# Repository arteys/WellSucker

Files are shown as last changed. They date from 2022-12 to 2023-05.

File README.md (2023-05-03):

# WellSucker
This project is dedicated to the development of silicone inserts in culture plastic. These will block cells from growing in a particular area, after which they are removed and it becomes possible to study the migration of cells to an empty site. I tried just flat silicone pieces, but they didn't hold well, especially in liquid. So now these things are arranged like suction cups. For 24 well plates, I made inserts with a diameter of 6 and 7 mm. There are some other options, but I'll post them later.

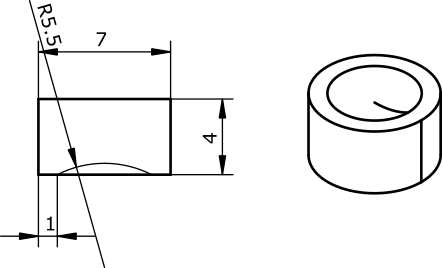
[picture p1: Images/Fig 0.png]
Sketch


To make such inserts, you need to print a mold on an MSLA 3D printer, and then pour two-component silicone into it. After hardening, the inserts are ready for use.

# 3d printing
I printed molds on a MSLA 3D printer (Anycubic Photon S) from a standard (Translucent Green) resin. For all printers and resins, different print settings are used, so there is not much point in applying mine here. Molds are printed strictly horizontally, flat, without any support. Printing at an angle greatly complicates the geometry of the parts due to the approximation of a complex shape by voxels, and the resulting inserts will not stick to the plastic reliably. Molds are designed in such a way that they are separated from the table without any problems.
There are different approaches to cleaning up objects after MSLA printing. I first wash them in dirty alcohol (IPA, although ET-OH also works fine), poured into a small container from IKEA, then for 15 minutes I wash it in an Anycubic Wash'n'Cure station in a slightly cleaner one. Finally, I flush them with a jet of alcohol from a squirt bottle and blow compressed air from a can (the one for cleaning computers) to remove all the alcohol.

Finally, I cure the objects in the same station (15 min), positioning them at such an angle that the ultraviolet accurately penetrates the cells. It is cells who must be reliably illuminated so that silicone does not stick to them later.

# The choice of silicone
This is the tricky part. Staying in the ideology of accessibility and DIY, I used the usual model two-component silicone available in the hobby store.
Two-component platinum-based silicones definitely do not work - there is some kind of reaction between the silicone and the printed part and the silicone does not polymerize.
Tin-based silicones remain, they generally work well. However, not all, I have met at least one that sticks to MSLA printed parts absolutely tightly and then it is impossible to separate the finished inserts. Accordingly, if someone decides to make such inserts, silicone will have to be selected empirically.
I didn't use any chemical separators because I didn't want to add their remnants to the biological medium.

## Step 1 and 2
Two-component silicone is mixed according to the manufacturer's instructions and poured into the wells. If the silicone is viscous, then the molds may have to be evacuated. I used a fairly fluid one, so there were no problems with bubbles.
However, if bubbles form in the finished inserts, they will spoil everything, in which case the molds with silicone must be evacuated. A certain amount of silicone may leave the wells - the most important thing is that their bottom is evenly covered, silicone can always be added after vacuuming.

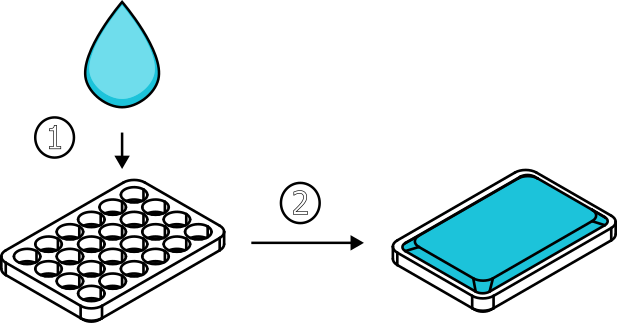
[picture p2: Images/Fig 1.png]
Step 1 and 2


## Step 3
But the next part requires some skill. With a wooden spatula (or any flat tool that you don’t mind throwing away later), you need to remove excess silicone, which will definitely be. The easiest way is to place the tool at an angle to the mold and, as it were, cut off all excess silicone. Ideally, the wells should be filled exactly to the edge, but no more. You can try to remove the excess with a cloth, but this is not very convenient.

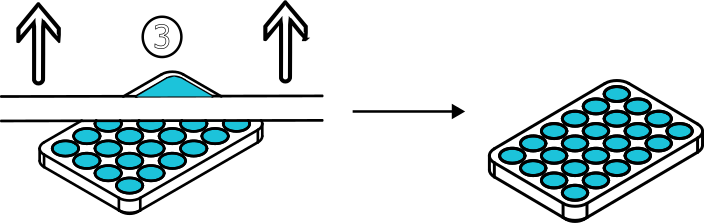
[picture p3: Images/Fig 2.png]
Step 3


After the silicone has hardened, the inserts can be removed with tweezers. Normally, they are removed quite easily, but if they stick so that they are torn to pieces, this silicone is probably not suitable.

## Inserts in cells of cultural plate
After being removed from the molds, the inserts can be sterilized with ethyl alcohol. I have not tried other methods of sterilization, although they certainly exist. Ethanol sterilization requires inserts to be placed in 70% ethanol for several minutes, after which they are removed, dried and placed in phosphate buffer or any other sterile liquid to remove residual ethanol.
Finally the inserts are ready to use. In order to install the insert into the cell of the plate, it is worth using tweezers. The most important thing is to determine where the insert has the top, it is more shiny, and the bottom is matte. Accordingly, the lower part of the insert is placed on the bottom of the well and gently pressed with tweezers from above. This is also a skill, however by the middle of the first 24 well plate it starts to come easy.
It is worth adding cells to the plate with relative accuracy. If you fill them too hard, you can wash off the insert, although this is unlikely.

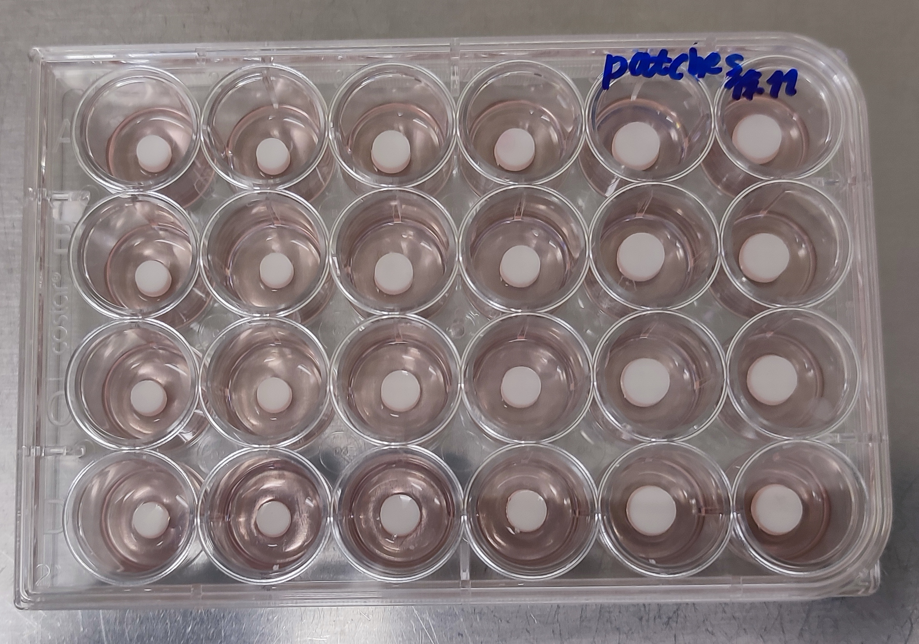
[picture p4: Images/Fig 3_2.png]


**WARNING:** These silicone inserts are amazingly bouncy. If they are pressed too hard and then released abruptly, they can jump to the other end of the laminar flow hood and fall into the vents.

## Inserts, view from the back of the plate
To make sure the inserts stick, you can turn the plate upside down. If the inserts are held securely they will of course not fall off if everything is done correctly.

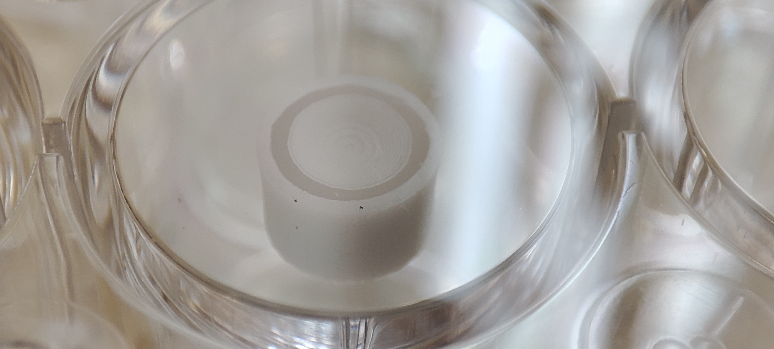
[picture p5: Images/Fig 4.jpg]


## Cells after removal of the insert
The next day, you can remove the inserts from the cells with tweezers and see something like this. I have not observed any significant cellular toxicity from silicone, but I may have been lucky with the choice of silicone. These are Vero culture cells, but experiments were also carried out with others cell lines.
Cells in plate

## Featured in
https://doi.org/10.3390/ijms24098150

## License
This project is open-source and is released under the CERN open hardware license. 
All files have been designed using  [FreeCAD](https://www.freecadweb.org/), illustrations made in FreeCAD and [Inkscape](https://inkscape.org/).

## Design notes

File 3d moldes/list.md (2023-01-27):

Model file for molds with a diameter of 6 and 7 mm

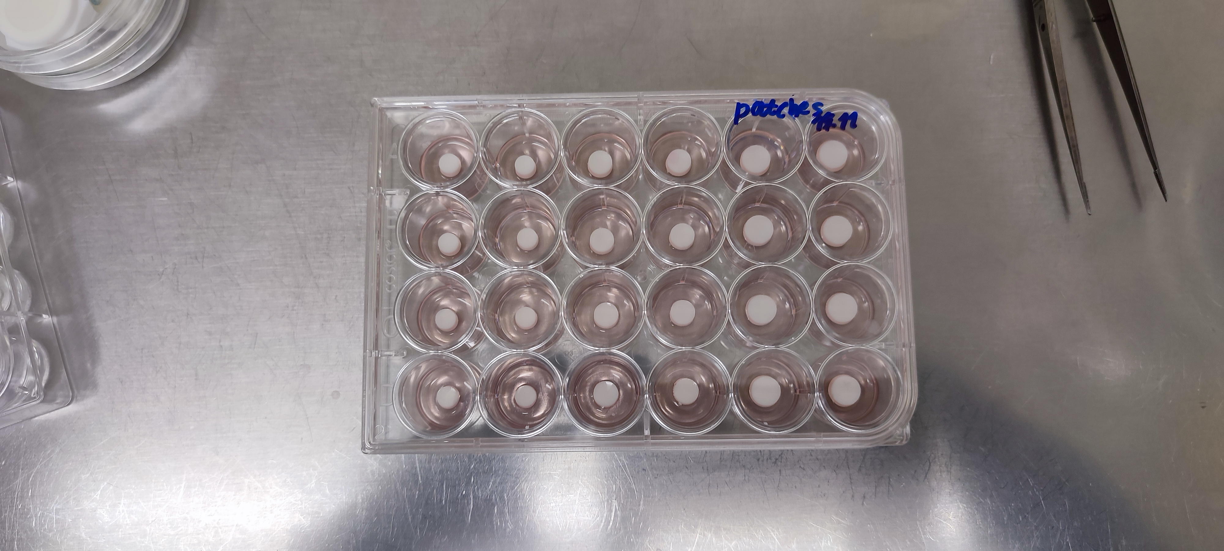
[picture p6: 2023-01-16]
Images/Fig 3.jpg

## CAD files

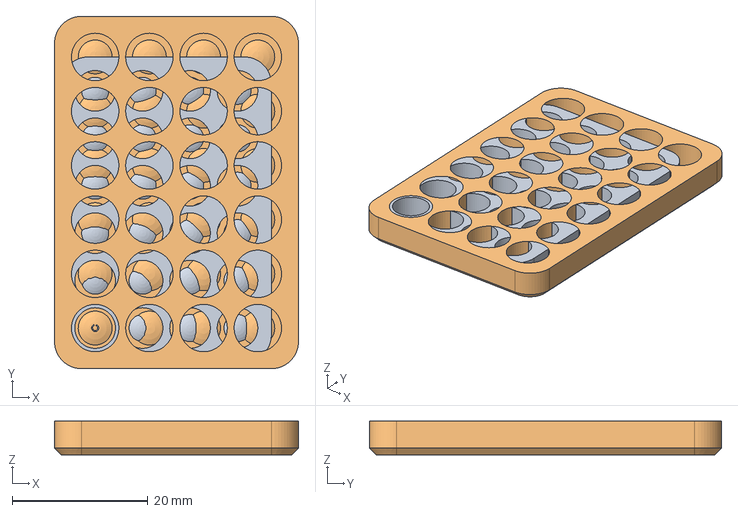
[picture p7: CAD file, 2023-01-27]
3d moldes/D6 and D7.FCStd
36.0 x 52.0 x 5.00 mm
D6
D7

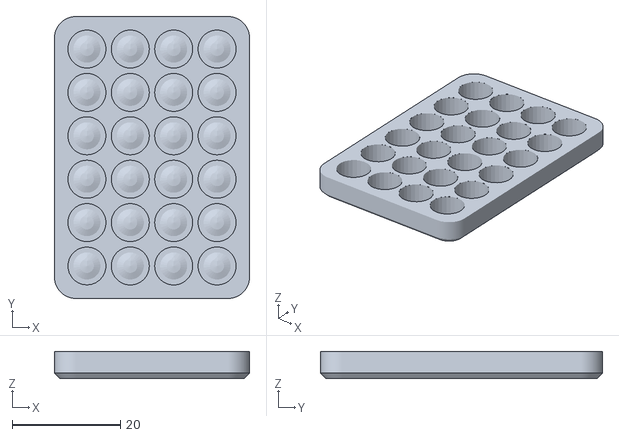
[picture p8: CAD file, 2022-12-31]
STL/D7 mold.stl
36.0 x 52.0 x 5.00

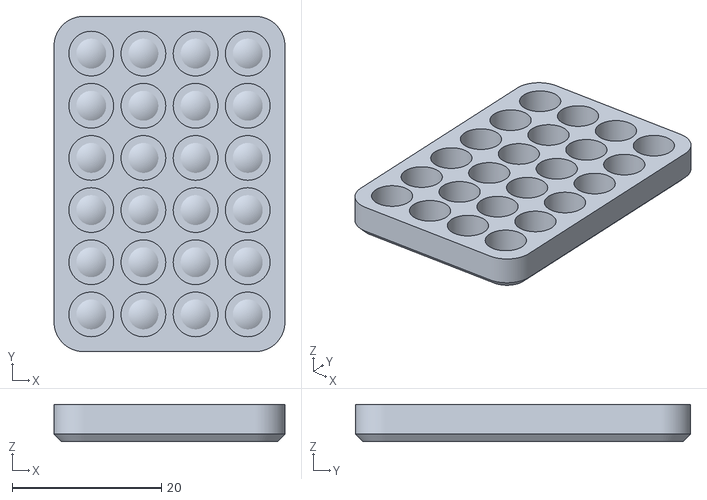
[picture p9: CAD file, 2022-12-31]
STL/D6 mold.stl
31.0 x 45.0 x 5.00

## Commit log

2023-01-16 Photos of inserts in the wildes
2023-01-25 New version of the plate with inserts photo
2023-01-27 3d models
    [D6 and D7.FCStd]
